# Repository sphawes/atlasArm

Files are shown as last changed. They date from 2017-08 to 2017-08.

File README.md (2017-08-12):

# ATLAS Arm - EMG Prosthetic Hand
The ATLAS (Articulating Tactile Limb Amputation Supplement) Arm is a 3D Printable, muscle-controlled prosthetic hand that can be manufactured for under $250 in consumable materials.

The ATLAS Arm started as an [IDEA Grant](http://ugradresearch.uconn.edu/idea/) project at the University of Connecticut by [Stephen Hawes](http://www.stephenhawes.com). Stephen documented the first six versions of the hand in a YouTube [video series](https://www.youtube.com/playlist?list=PLIeJXmcg1baLB6wgaJ4MkH0-Whnp8Us2D).

## Instructions
The ATLAS Arm was designed to be completely customizable for any mid-forearm amputee to use. Only a few tools are necessary to create one at home, and about $250 in materials, all listed in the Bill of Materials document.

1. Using the Advancer Technologies EMG sensor, test sensor pad locations using the test.ino script in the CAD folder in the Github Repo. Description of how this is done is a comment at the top of the findPadLocation.ino file. Once you've found the ideal locations, mark the Reference, End, and Middle of the muscle with R, E, and M respectively. Do so with a fine-point Sharpie in small text.

2. Using Skanect and the Kinect sensor, take a 3D scan of the remaining forearm of the amputee for which the arm is being made. Take two scans: One with a 90 degree bend at the elbow, and another with the forearm straight. Save as an .obj file.

3. Take 8 measurements of the amputee's remaining hand using millimeters as a unit. These measurements are as follows:
    - P1 - distance from the rotational center of the third knuckle to the rotational center of the second knuckle on the index finger.
    - Px - Width of the palm (from base of index finger to base of pinky).
    - Py - Length of the palm (from wrist to third knuckle).
    - Pz - Thickness of the palm.
    - Wx - Width of wrist (in direction of thumb to pinky).
    - Wz - Thickness of wrist.
    - Ff - Full length of forearm (from wrist to rotational center of the elbow).
    - Fa - Length of remaining forearm (from end of amputation to rotational center of the elbow.)

4. Load the "Atlas Arm" Fusion 360 file. Save your own copy of the file to your Autodesk cloud and rename it to the name of the amputee, or some other distinguishable title. Then, edit the new file in the following ways:
    - Under the "Modify" menu, select "Change Parameters" option with the sigma icon.
    - Enter in your new values for Px, Py, Pz, P1, Wx, and Wz.
    - If the model fails to render, it is possible that the design does not scale properly for the dimensions given. The timeline at the bottom can be rolled back to see where the error occurred, and fixed.

5. Export the following components as separate STL files: 1, 2, 3, 4, 5, 1joints, 2joints, 3joints, 4joints, 5joint, palm, and palmJoints. This can be done by clicking on the component in the list on the left, then clicking "3D Print" in the "Make" menu.

6. 3D print the fingers and the palm. Each print requires dual extrusion with the second nozzle extruding Ninjaflex. Print files 1 and 1joints together, 2 and 2joints together, etc. with the joints file being printed in Ninjaflex and the other part printed in ABS. It is recommended to use a Lulzbot Taz with a FlexyDually Extruder.

7. 3D print the Base Unit. This can be exported in the same fashion as the fingers from Fusion 360. Print in PLA plastic.

8. 3D print the socket component. The socket should be printed in Ninjaflex, and the outer shell printed in ABS plastic, using a dual extrusion printer. It is recommended to use a Lulzbot Taz with a Flexydually Extruder.

9. Assemble the hand.
    - Insert M4 heat-set inserts into the back of each finger using a soldering iron until the insert is completely clear of the slot for the Ninjaflex joint.
    - Slide each finger onto their respective Ninjaflex joints and secure the fingers using an M4x10mm machine screw and a M4 washer. You will have to puncture the Ninjaflex joint before attempting to screw through it.
    - String up each finger. Cut five lengths of fishing line one foot long, and feed them from the tip of each finger into the motor cavity in the back of the palm. Tie off the fishing line at the tip of each finger with a loose knot, but do not cut off the excess.
    - Solder the leads of the motor to the appropriate pins on the motor driver board, and glue the spool onto the spindle of the motor using CA glue. Glue the ends of the five lengths of fishing line to the inside of the spool. After drying, wrap the cabling once more around the spool and fit the motor into it's cavity.
    - Loosen the knots at the ends of the fingers, and tighten each one so that each finger is slightly bent forward and under tension. Glue the knots secure with CA glue and trim the excess.
    - Wire the necessary pins from the motor driver to the pinout at the base of the palm, then glue the pinout into place.

10. Make the Core Module. Follow the schematic in the "Hardware" folder using parts from the Bill of Materials. Print the enclosure and cap for the Core Module found in the "CAD" folder. Use the CAD model in Fusion 360 as reference.

11. Edit firmware. A few example firmware files are provided. If the device will only be using the standard ATLAS Arm prosthetic hand attachment, then "firmwareHandOnly.ino" can be used as is.

12.

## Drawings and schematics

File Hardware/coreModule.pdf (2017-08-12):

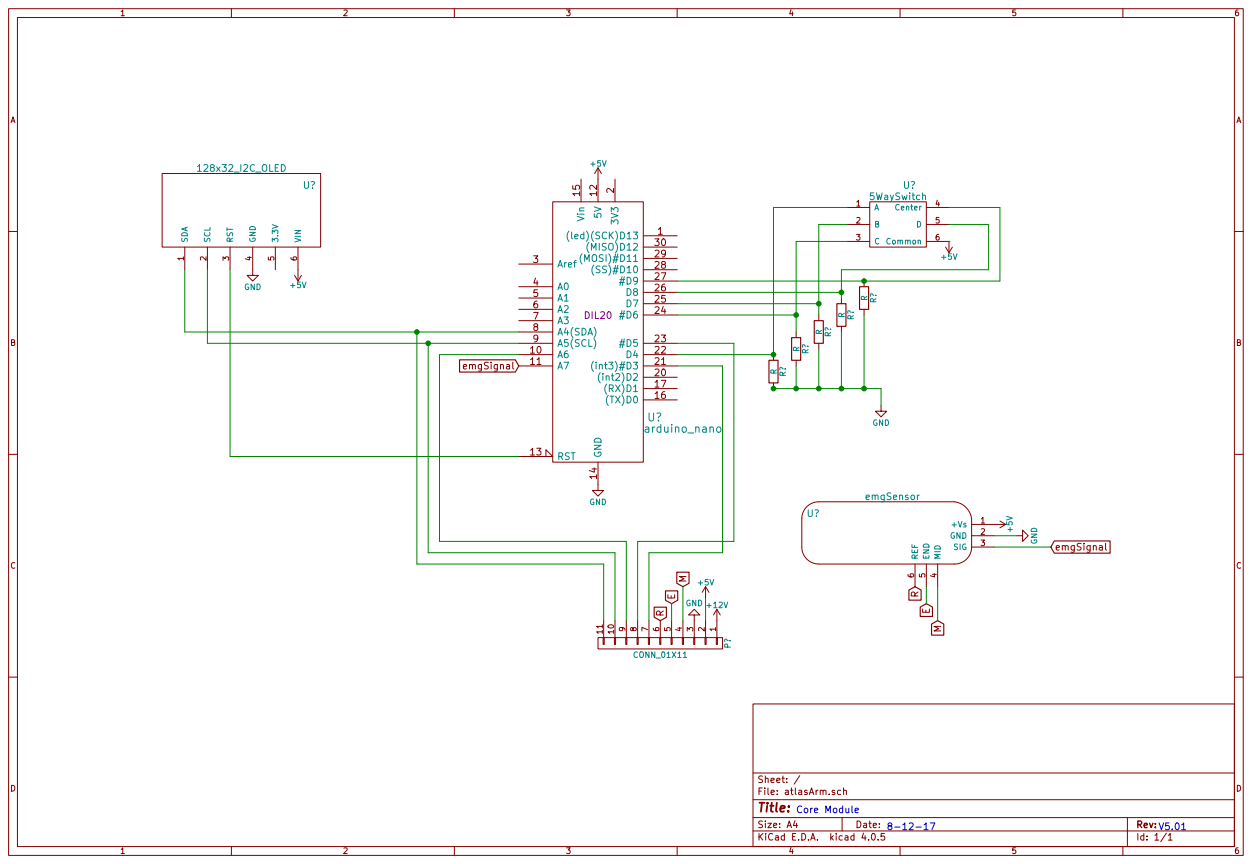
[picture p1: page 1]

Id: 1/1 Title: File: atlasArm.sch Sheet: / GND 14 Vin 15

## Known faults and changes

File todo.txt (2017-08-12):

-add eeprom functionality
-finish readme
-export standard stl files and save to CAD folder
-finish building version 5

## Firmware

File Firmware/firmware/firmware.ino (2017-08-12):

/*
Atlas Laboratories, LLC
Written by Stephen Hawes
Atlas Arm V5.0
Standard Hand Firmware
*/

/*
Copyright (c) 2017 Stephen Hawes

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
THE SOFTWARE IS PROVIDED "AS IS", WITHOUT WARRANTY OF ANY KIND, EXPRESS OR
IMPLIED, INCLUDING BUT NOT LIMITED TO THE WARRANTIES OF MERCHANTABILITY,
FITNESS FOR A PARTICULAR PURPOSE AND NONINFRINGEMENT. IN NO EVENT SHALL THE
AUTHORS OR COPYRIGHT HOLDERS BE LIABLE FOR ANY CLAIM, DAMAGES OR OTHER
LIABILITY, WHETHER IN AN ACTION OF CONTRACT, TORT OR OTHERWISE, ARISING FROM,
OUT OF OR IN CONNECTION WITH THE SOFTWARE OR THE USE OR OTHER DEALINGS IN THE
SOFTWARE.
*/

/* Pin Reference
 * A4 - I2C Data / Hitch Analog Pin
 * A5 - I2C Clock / Hitch Analog Pin
 * A6 - Hitch Analog Pin
 * A7 - EMG Signal
 * D3 - PWM / Interrupt / Hitch Digital Pin
 * D5 - PWM / Hitch Digital Pin
 *
 * D4 - Joy Up (A)
 * D6 - Joy Down (C)
 * D7 - Joy Left (B)
 * D8 - Joy Right (D)
 * D9 - Joy Center Press (Center)
 *
 *
 */

/*
 *
 *  LIBRARIES
 *
 */
//These libraries are from Adafruit that run the screen driver
#include <Adafruit_SSD1306.h>
#include <Adafruit_GFX.h>
#include <SPI.h>
#include <Wire.h>
//For storing calibration values
#include <EEPROM.h>
//For controlling grip strength
#include <PID_v1.h>



static const unsigned char PROGMEM logo16_glcd_bmp[] =
{ B11111111, B11111111, B11111111, B11111111, B11111111, B11111111, B11111111, B11111111, B11111111, B11111111, B11111111, B11111111, B11111111, B11111111, B11111111, B11111111,
  B10000000, B00000000, B00000000, B00000000, B00000000, B00000000, B00000000, B00000000, B00000000, B00000000, B00000000, B00000000, B00000000, B00000000, B00000000, B00000001,
  B10000000, B00000000, B00000000, B00000000, B11111110, B00000000, B00000000, B00000000, B00000000, B00000000, B00000000, B00000000, B00000000, B00000000, B00000000, B00000001,
  B10000000, B00000000, B00000000, B00000011, B11111111, B10000000, B00000000, B00000000, B00000000, B00000000, B00000000, B00000000, B00000000, B00000000, B00000000, B00000001,
  B10000000, B00000000, B00000000, B00001111, B00000001, B11100000, B00000000, B00000000, B00000000, B00000000, B00000000, B00000000, B00000000, B00000000, B00000000, B00000001,
  B10000000, B00000000, B00000000, B00011100, B00000000, B01110000, B00000000, B00000000, B00000000, B00000000, B00000000, B00000000, B00000000, B00000000, B00000000, B00000001,
  B10000000, B00000000, B00000000, B00111000, B00000000, B00111000, B00000001, B10001001, B00000000, B00000000, B00000000, B00000000, B00000000, B00000000, B00000000, B00000001,
  B10000000, B00000000, B00000000, B00110000, B00000000, B00011000, B00000001, B10001001, B00000000, B00000000, B00000000, B00000000, B00000000, B00000000, B00000000, B00000001,
  B10000000, B00000000, B00000000, B01100000, B00000000, B00001100, B00000011, B11011101, B00111000, B11100000, B00000000, B00000000, B00000000, B00000000, B00000000, B00000001,
  B10000000, B00000000, B00000000, B01100000, B00000000, B00001100, B00000010, B01001001, B00001001, B00000000, B00000000, B00000000, B00000000, B00000000, B00000000, B00000001,
  B10000000, B00000000, B00000000, B11000000, B00000000, B00000110, B00000011, B11001001, B00111000, B11000000, B00000000, B00000000, B00000000, B00000000, B00000000, B00000001,
  B10000000, B00000000, B00000000, B11000000, B00000000, B00000110, B00000110, B01101001, B01001000, B00100000, B00000000, B00000000, B00000000, B00000000, B00000000, B00000001,
  B10000000, B00000000, B00000000, B11000000, B00000000, B00000110, B00000100, B00101101, B01111101, B11000000, B00000000, B00000000, B00000000, B00000000, B00000000, B00000001,
  B10000000, B00000000, B00000000, B11000000, B00000000, B00000110, B00000000, B00000000, B00000000, B00000000, B00000000, B00000000, B00000000, B00000000, B00000000, B00000001,
  B10000000, B00000000, B00000000, B11000000, B00010000, B00000110, B00000000, B00000000, B00000000, B00000000, B00000000, B00000000, B00000000, B00000000, B00000000, B00000001,
  B10000000, B00000000, B00000000, B11000000, B00010000, B00000110, B00000000, B00000000, B00000000, B00000000, B00000000, B00000000, B00000000, B00000000, B00000000, B00000001,
  B10000000, B00000000, B00000000, B11000000, B00111000, B00000110, B00000000, B00000000, B00000000, B00000000, B00000000, B00000000, B00000000, B00000000, B00000000, B00000001,
  B10000000, B00000000, B00000000, B01100000, B00111000, B00001100, B00000100, B00000000, B01000000, B00000000, B00001000, B00000000, B10000000, B00000000, B00000000, B00000001,
  B10000000, B00000000, B00000000, B01100000, B01010100, B00001100, B00000100, B00000000, B01000000, B00000000, B00001000, B00000000, B00000000, B00000000, B00000000, B00000001,
  B10000000, B00000000, B00000000, B00110000, B01010100, B00011000, B00000100, B00001110, B01110001, B10011101, B11011100, B11001110, B10011100, B01110000, B00000000, B00000001,
  B10000000, B00000000, B00000000, B00111000, B11010110, B00111000, B00000100, B00000010, B01001010, B01010000, B01001001, B00101000, B10100010, B10000000, B00000000, B00000001,
  B10000000, B00000000, B00000000, B00011100, B10010010, B01110000, B00000100, B00001110, B01001010, B01010001, B11001001, B00101000, B10111110, B01100000, B00000000, B00000001,
  B10000000, B00000000, B00000000, B00001111, B10010011, B11100000, B00000100, B00010010, B01001010, B01010010, B01001001, B00101000, B10100000, B00010000, B00000000, B00000001,
  B10000000, B00000000, B00000000, B00000011, B11111111, B10000000, B00000111, B11011111, B01110001, B10010011, B11101100, B11001000, B10011100, B11100000, B00000000, B00000001,
  B10000000, B00000000, B00000000, B00000000, B01111100, B00000000, B00000000, B00000000, B00000000, B00000000, B00000000, B00000000, B00000000, B00000000, B00000000, B00000001,
  B10000000, B00000000, B00000000, B00000011, B00000001, B10000000, B00000000, B00000000, B00000000, B00000000, B00000000, B00000000, B00000000, B00000000, B00000000, B00000001,
  B10000000, B00000000, B00000000, B00000111, B10111011, B11000000, B00000000, B00000000, B00000000, B00000000, B00000000, B00000000, B00000000, B00000000, B00000000, B00000001,
  B10000000, B00000000, B00000000, B00000111, B00111001, B11000000, B00000000, B00000000, B00000000, B00000000, B00000000, B00000000, B00000000, B00000000, B00000000, B00000001,
  B10000000, B00000000, B00000000, B00000001, B00111001, B00000000, B00000000, B00000000, B00000000, B00000000, B00000000, B00000000, B00000000, B00000000, B00000000, B00000001,
  B10000000, B00000000, B00000000, B00000000, B00000000, B00000000, B00000000, B00000000, B00000000, B00000000, B00000000, B00000000, B00000000, B00000000, B00000000, B00000001,
  B10000000, B00000000, B00000000, B00000000, B00000000, B00000000, B00000000, B00000000, B00000000, B00000000, B00000000, B00000000, B00000000, B00000000, B00000000, B00000001,
  B11111111, B11111111, B11111111, B11111111, B11111111, B11111111, B11111111, B11111111, B11111111, B11111111, B11111111, B11111111, B11111111, B11111111, B11111111, B11111111
  };



//Defining joystick digital pins
#define joyUp       4
#define joyDown     6
#define joyLeft     7
#define joyRight    8
#define joyPress    9

//Defining analog pins
#define sphA1  A4
#define sphA2  A5
#define sphA3  A6
#define emg    A7

//Defining digital pins
#define sphD1  3
#define sphD2  5

//Defining size of EMG Cache
#define emgCacheSize  10

#define OLED_RESET A1


/* Holds position of current menu.
 *  0=main menu
 *  1=hand menu
 *  2=solder menu
 *  3=threshold menu
 *  4=hand select menu
 *  5=version menu
 *  6=calibrate menu
 */
int currentMenu = 0;
int currentWidth = 0;
int currentHand = 0;
bool motorTestStatus = false;
bool logoViewStatus = false;

//Joystick variables
int joyMemory = 0;

//EMG variables
int emgCache[emgCacheSize] = {0,0,0,0,0,0,0,0,0,0};
int newEmg = 0;
float avgEmg = 0;
int emgCachePosition = 0;
int summedCache = 0;
int state = 0; //0 for open, 1 for light squeeze, 2 for hard squeeze
int oldState = 0;

//EEPROM
//address in eeprom is 0
int eepromThreshold1 = 530;
//EEPROM.read(0);
//address in eeprom is 1
//int eepromThreshold2 = 90;
//EEPROM.read(1);
//address in eeprom is 2
int eepromNeutral = 0;
//EEPROM.read(2);

//PID
int PIDstate = 0;
double Kp = 2;
double Ki = 5;
double Kd = 1;
double handSetpoint = 150;
double input = 0;
double output = 0;

//PID
PID handPID(&input, &output, &handSetpoint, Kp, Ki, Kd, DIRECT);

//Display
Adafruit_SSD1306 display(OLED_RESET);

void setup() {

  //Serial
  Serial.begin(9600);
  Serial.println("ATLAS ARM V5.0");

  //Display

  display.begin(SSD1306_SWITCHCAPVCC, 0x3C);
  display.clearDisplay();
  display.drawBitmap(0, 0,  logo16_glcd_bmp, 128, 32, 1);
  display.display();
  delay(1000);
  display.clearDisplay();
  loadHandMenu(0);

  handPID.SetMode(AUTOMATIC);

}

void loop() {
  //main loop of OS!

  //serial out a bit of data for diagnostics
  Serial.print("Menu: " + currentMenu);
  Serial.println(" Width: " + currentWidth);

  //checking joystick and changing (and displaying) menu accordingly
  int joy = checkJoy();
  if(joyMemory != 0 && joy == 0){
    joyMemory = 0;
  }
  if (joy != joyMemory && joy != 0){
    changeMenu(joy);
    joyMemory = joy;
  }

  //running loops for specific menus
  if(currentMenu == 0 && currentWidth == 0){ //if on standard hand menu
    standardHandControl();
  }
  else if(currentMenu == 0 && currentWidth == 1){ //if on solder hand menu
    solderHandControl();
  }
  else if(currentMenu == 0 && currentWidth == 2){
    bikeHandControl();
  }
  else if(motorTestStatus){
    runPidHand();
  }
}
//END MAIN OS LOOP


int checkJoy(){
  //check joy returns an integer representing which direction the joystick is pointing. 0 for neutral, 1 for up, 2 for right, 3 for down, and 4 for left
  int upBit = digitalRead(joyUp);
  int downBit = digitalRead(joyDown);
  int leftBit = digitalRead(joyLeft);
  int rightBit = digitalRead(joyRight);
  int pressBit = digitalRead(joyPress);

  if(upBit){
    return 1;
  }
  else if(downBit){
    return 3;
  }
  else if(leftBit){
    return 4;
  }
  else if(rightBit){
    return 2;
  }
  else if(pressBit){
    return 5;
  }
  else{
    return 0;
  }

}

void standardHandControl(){
  /* loop run through for normal atlas arm peripheral
   * D3 is pwm
   * D5 is direction
   * A6 is current sense
   */

  //Gather and analize emg data to update "setpoint" variable which will come into effect in Motor segment below
  updateEmgAvg();
  Serial.println(avgEmg);
  if(avgEmg < eepromThreshold1){
    state = 0;
  }
  else{
    state = 1;
  }

  if(oldState == 0 && state == 1){ //think: only on the rising edge
    delay(100);
    for(int i=0;i<10;i++){
      updateEmgAvg();
    }
    if(avgEmg > eepromThreshold1){
      if(handSetpoint == 0){
        handSetpoint = 150;
      }
      else{
        handSetpoint = 0;
        //spin backwards slightly to open hand
        digitalWrite(5, LOW);
        analogWrite(3, 100);
        delay(100);
        analogWrite(3, 0);
      }
    }
    else{
      state = 0;
    }
  }

  oldState = state;

  //Change Motor PID in accordance with changes in EMG segment above

  runPidHand();

}

void solderHandControl(){
  digitalWrite(3, HIGH);
  delay(10);
  digitalWrite(3, LOW);
  delay(10);
}

void bikeHandControl(){
    digitalWrite(5, HIGH);
    delay(10);
    digitalWrite(5, LOW);
    delay(10);
}

//gets new emg value, replaces oldest emg value in cache, averages the cache, and saves the average to avgEmg
void updateEmgAvg(){
  //bring in new emg data point and add to cache.
  newEmg = analogRead(A7);
  summedCache = summedCache - emgCache[emgCachePosition];
  summedCache = summedCache + newEmg;

  emgCache[emgCachePosition] = newEmg;
  if(emgCachePosition == (emgCacheSize - 1)){
    emgCachePosition = 0;
  }
  else{
    emgCachePosition++;
  }

  avgEmg = summedCache / emgCacheSize;

}

/*
*
* Ok, here's the PID function.
* This function reads the analog pin,
*
*/
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

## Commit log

2017-06-16 general update, made firmware for v4 work with adafruit 32x128 oled led screen
2017-06-16 updated bike and solder menus to make d3 and d5 high and low pulse for identification to make sure i wired the pins correctly
2017-07-30 switched all of github content to version 5
    [Atlas Arm V3 v21.iges, AtlasArmBACKUP.iges, AtlasArmBACKUP.step, dorsalV1.0.stl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]
2017-07-30 added kicad directory and starting files
    [atlasArm.kicad_pcb, atlasArm.sch]
2017-08-12 finished main wiring of core module schematic. kicad rocks
    [_saved_atlasArm.sch, atlasArm.sch]
2017-08-12 added todo text file, added pdf of schematic V5.01
    [atlasArm.sch]
